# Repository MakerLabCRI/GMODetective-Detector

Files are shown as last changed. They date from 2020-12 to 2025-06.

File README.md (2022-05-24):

# GMODetective-Detector

DIY fluorescence detector for the [GMO Detective project](https://gmodetective.com/)

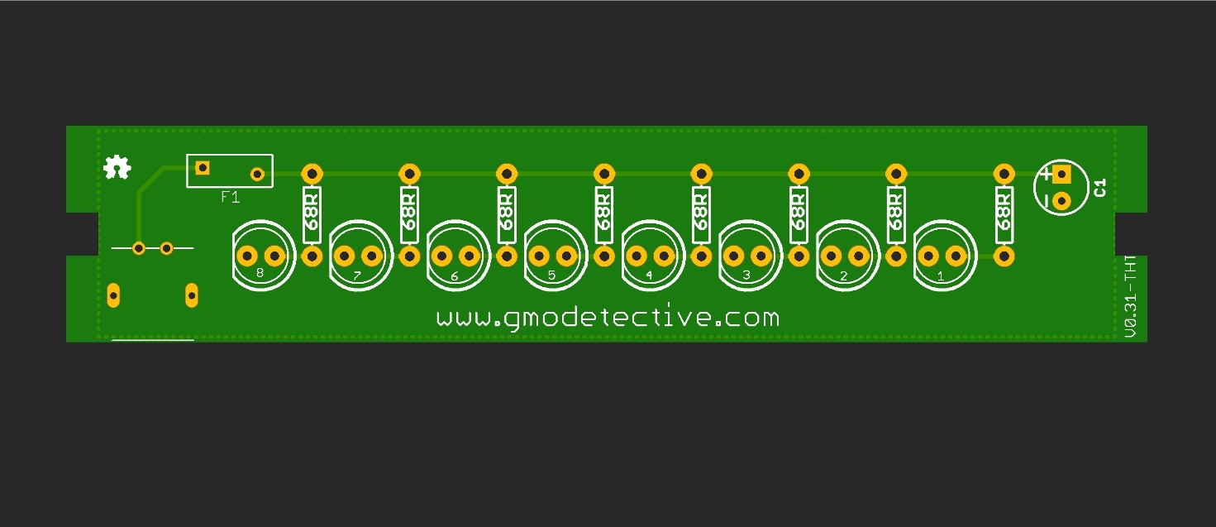
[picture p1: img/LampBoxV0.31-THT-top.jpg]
PCB view


## BOM

8x C503B-BAN-CZ0A0451 [mouser](https://www.mouser.fr/ProductDetail/Cree-Inc/C503B-BAN-CZ0A0451?qs=%2Fha2pyFaduidizlAeORLOPChSupn8qVQ9Kn4bl13zJ7nUG9%252B2UeDbT0K%252B9FgAF1f)

8x 68 ohm resistor [mouser](https://www.mouser.fr/ProductDetail/Yageo/CFR-25JT-52-68R?qs=%2Fha2pyFaduip15hodXcAQzG82qC8UTcP%2FVcFQd8KsgKmaA7VFXCJAQ%3D%3D)

1x 10uF electrolytic capacitor [mouser](https://www.mouser.fr/ProductDetail/Panasonic/ECA-1JM100B?qs=%2Fha2pyFadugf96c9oovEvKSc4mhyX5s0jUH4ND99LTDADYv5TkhqzA%3D%3D)

1x Fuse 500ma RXEF050 [mouser](https://www.mouser.fr/ProductDetail/Littelfuse/RXEF050?qs=k5V78Jg%2Feq7BserVMEB6DA%3D%3D)

1x micro USB 2P with 90° pins [Taobao](https://item.taobao.com/item.htm?spm=a230r.1.14.68.312b6bc3MnUb4G&id=597273597165&ns=1&abbucket=19#detail)
[Aliexpress](https://fr.aliexpress.com/item/4000049679173.html?spm=a2g0o.productlist.0.0.6fd1f912MCE4d2&algo_pvid=a3873bf6-c53e-42d9-8363-89ecb1d975f8&algo_expid=a3873bf6-c53e-42d9-8363-89ecb1d975f8-4&btsid=0b0a182b16071189178941562e2389&ws_ab_test=searchweb0_0,searchweb201602_,searchweb201603)
[Aliexpress (90 ° version color B or D)](https://aliexpress.com/item/4001293555150.html)
[Aliexpress (90° version color A or C)](https://fr.aliexpress.com/item/1005001515820458.html)

## 3D Model of PCB

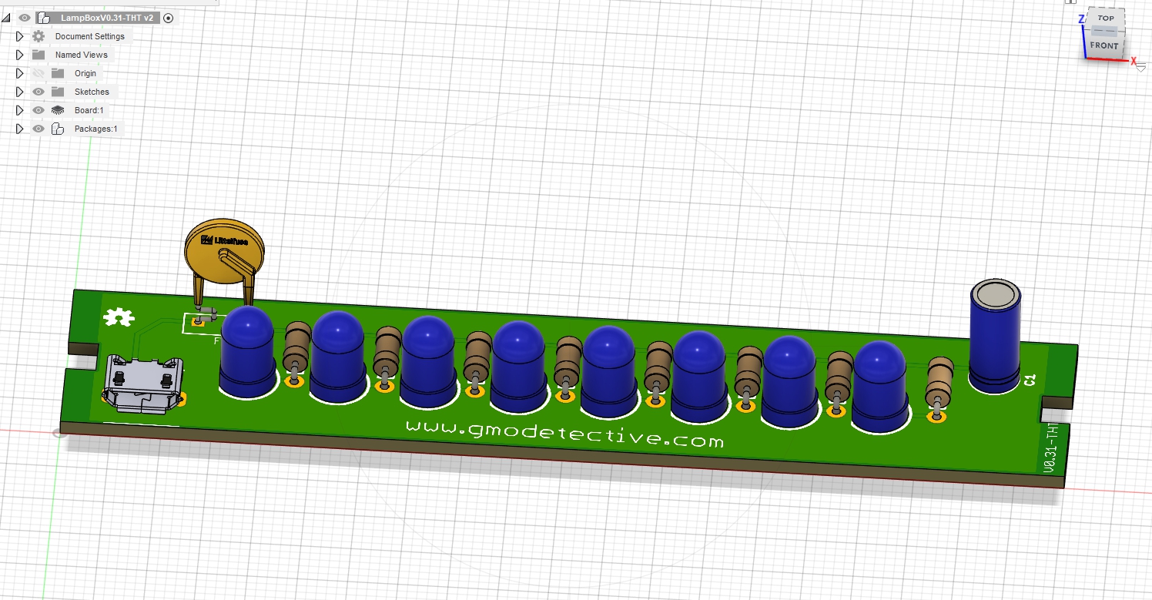
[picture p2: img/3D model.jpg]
Screengrab of 3d model


3D model

## 3d printable frame

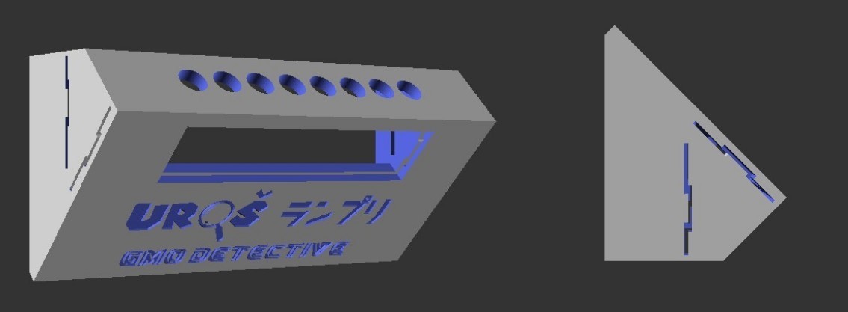
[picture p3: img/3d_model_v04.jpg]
3d model filter slit version


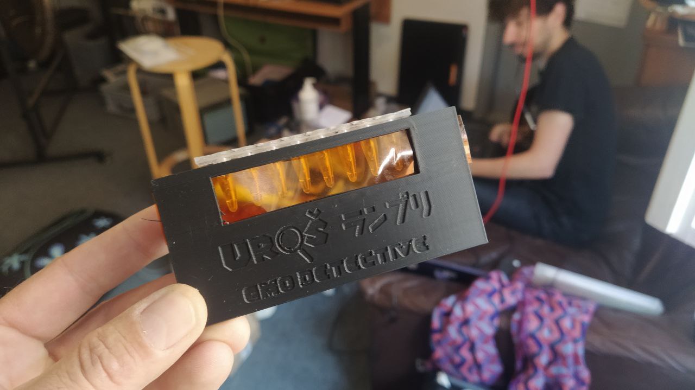
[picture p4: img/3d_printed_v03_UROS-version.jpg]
3d printed UROS version


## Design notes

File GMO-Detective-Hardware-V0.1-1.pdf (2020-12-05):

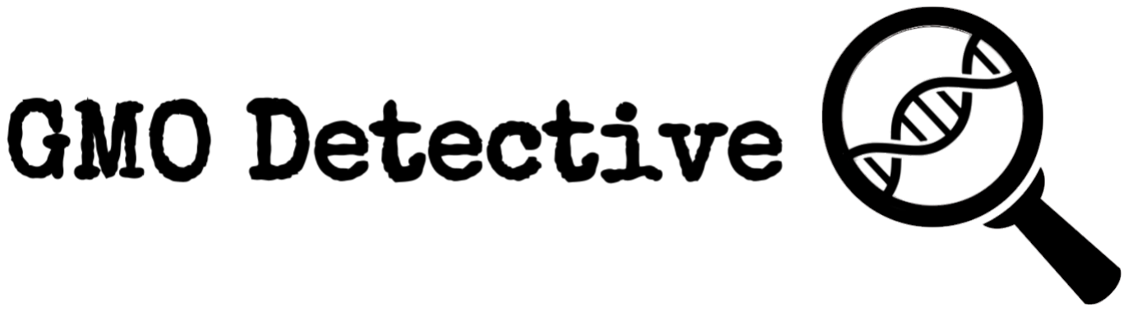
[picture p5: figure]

# Hardware Guide:

The Hardware guide will help you to gather, buy and build all the materials you need to do the experiments. This consists of reusable devices such as the open hardware fluorescence detector and also consumables which are used with each experiment.

Reusables | 1
Makabales | 1
Open Hardware Detector | 1
Holders | 2
Buyable or makeable or hackable | 3
Common materials anyone probably has: | 3
Stable heating: | 3
20 µL Pipettes | 3
Consumables | 4

# Reusables

## Makabales

Files for PCB and Laser cutter: https://gmodetective.com/wp-content/uploads/2018/10/GMOdetective_Hardware_FilesV0.1.zip (https://gmodetective.com/wp-content/uploads/2018/10/GMOdetective_Hardware_FilesV0.1.zip)

### a. Open Hardware Detector

This is a cheap DIY fluorescence detector. It is easy to build and use. A buyable version should be available soon. You will need to know how to solder as well as a soldering iron, 15x15cm 3mm plexiglass/wood, a laser cutter and the following parts:

1 PCB | https://www.pcbway.com The file is in eagle format (free for students) We can also send you some :)
8 5mm blue LEDs 470nm | https://www.mouser.com/_/?Keyword=C503B-BAN-CZ0A0451
8 68/100 ohms resistors | https://www.mouser.com/_/?Keyword=CFR-25JT-52-68R
1 Capacitor 10 F | https://www.mouser.com/_/?Keyword=ECA-1JM100B
1 Fuse 0,5 A | https://www.mouser.com/_/?Keyword=RXEF025

Orange Filters | 179 Chrome Orange ; http://www.leefilters.com/lighting/colour-details.html#179
Blue Filter | 716 Mikkel Blue : http://www.leefilters.com/lighting/colour-details.html#716

Solder the parts onto the PCB
Laser-cut the legs tube holder and front panel
Slide the PCB into the Legs
Then attach front panel and top tube holder.
Slide 1.5x11cm blue filter into leg side slits, and 2 orange filters into the smale space between the legs and front panel so you see orange through the view hole Connect to a 5v power source (USB).

### b. Holders

Laser-cut the legs and tube holder and connect

## Buyable or makeable or hackable

### Common materials anyone probably has:

You will need a mug or beaker to hold boiling water for 5 minutes during the sample prep, anything that can hold coffee or tea will do.
Aluminum foil to hold the tubes in place.
Permanent waterproof markers too, so you know what is what :)

### Stable heating:

We need something that can keep a stable 63℃

If you have a PCR machine/heat block/Scientific water bath then these will all be perfect.
Otherwise these portable sous vide vacuum cookers are perfect and affordable, and you can also experiment with new ways of cooking! https://www.aliexpress.com/item/Vacuum-Slow-Sous-Vide-Precision-Food-Cooker-1500W-Powerful-Immersion-Circulator-LCD-Digital-Timer-Display-Stainless/32869232621.html?spm=a2g0s.8937460.0.0.302d2e0eDrMWuV (https://www.aliexpress.com/item/Vacuum-Slow-Sous-Vide-Precision-Food-Cooker-1500W-Powerful-Immersion-Circulator-LCD-Digital-Timer-Display-Stainless/3286923262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)
Or

https://anovaculinary.com/
Or

### You can also make one yourself! https://www.instructables.com/howto/sous+vide/ https://www.instructables.com/id/DIY-Sous-Vide-Machines/

### 20 µL Pipettes

Buy:
https://www.aliexpress.com/item/2-20ul-Single-Channel-Adjustable-Micro-Pipette-Transfer-Pipette-Lab-Pipettor-Buy-1-Pipette-Give-50pcs/3281466128 7.html (https://www.aliexpress.com/item/2-20ul-Single-Channel-Adjustable-Micro-Pipette-Transfer-Pipette-Lab-Pipettor-Buy-1-Pipette-Give-50pcs/32814661287.html)

# Consumables

These you will need to buy. Every experiment needs: ~4 1.5mL tubes
1 PCR strip
2 Pestles
2 gloves
And ~10 tips

1,5 mL microtubes | https://www.aliexpress.com/item/1-5ml-Clear-plastic-centrifugal-t est-tube-Sample-vial-with-snap-cap-for-samples-food-colourings /32694400420.html?spm=a2g0s.9042311.0.0.3da24c4dcV9Hma (https://www.aliexpress.com/item/1-5ml-Clear-plastic-centrifugal-test-tube-Sample-vial-with-snap-cap-for-samples-food-colourings/32694400420.html)
PCR 8 tube Strips | https://www.aliexpress.com/item/200PCS-4ml-Centrifuge-Bottles-Test-Tube-With-Lid-Calibration-Round-Bottom-Seed-Container-Laboratory-Supplies-1500r/32708099906.html?spm=a2g0s.9042311.0. 0.3da24c4dcV9Hma (https://www.aliexpress.com/item/200PCS-4ml-Centrifuge-Bottles-Test-Tube-With-Lid-Calibration-Round-Bottom-Seed-Container-Laboratory-Supplies-1500r/32708099906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)
micropestles | https://www.aliexpress.com/item/50-pcs-lot-5mm-70mm-Polypropylene-Pestle-grinding-PP-rod-tip-for-1-5ml-centrifuge-tube/327620

70308.html?spm=2114.search0104.3.2.2ee51276oXfHhu&ws_ab_test= searchweb0_0,searchweb201602_3_10152_10151_10065_10344_10068_1 0342_10343_10340_10341_10696_310_10084_10083_10618_10304_10307_1 0820_10821_10302_10843_10059_100031_10103_10624_10623_10622_10621 _10620_526,searchweb201603_13,ppcSwitch_5&algo_expid=9a04db1 4-5032-4917-9edd-e21168868e7b-0&algo_pvid=9a04db14-5032-4917-9edd-e21168868e7b&priceBeautifyAB=0 (https://www.aliexpress.com/item/50-pcs-lot-5mm-70mm-Polypropylene-Pestle-grinding-PP-rod-tip-for-1-5ml-centrifuge-tube/32762070308.html?priceBeautifyAB=0)

Pipet Tips

https://www.aliexpress.com/item/New-200ul-PP-Plastic-Pipette-Tip s-For-Microbiological-Test-Pipettor-Yellow-Pipet-Tips-Disposable -Pipette-Tip/32523839777.html?spm=2114.10010108.1000014.1.6f52221c D5FWBa&gps-id=pcDetailBottomMoreOtherSeller&scm=1007.13338 .107646.000000000000000&scm_id=1007.13338.107646.00000000000000 0&scm-url=1007.13338.107646.000000000000000&pvid=982c463a-c9c 4-40ca-9c91-248ec5df68f3 (https://www.aliexpress.com/item/New-200ul-PP-Plastic-Pipette-Tips-For-Microbiological-Test-Pipettor-Yellow-Pipet-Tips-Disposable-Pipette-Tip/32523839777.html?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)

Pipet Tips in Box

https://www.aliexpress.com/item/Free-shipping-Plastic-Pipette-box-96vents-box-96pcs-200ul-yellow-pipette-tips/32595675105.html?spm=2114.10010108.1000013.1.4569761fII1muL&gps-id=pcDetailBottomMoreThisSeller&scm=1007.13339.90158.0&scm_id=1007.13339.90158.0&scm-url=1007.13339.90158.0&pvid=96b5e6cb-d67c-4218-96ed-4ef54 2c1ffcf (https://www.aliexpress.com/item/Free-shipping-Plastic-Pipette-box-96vents-box-96pcs-200ul-yellow-pipette-tips/32595675105.html?scm_id=1007.13339.90158.0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)

gloves

https://www.aliexpress.com/item/3-Sizes-High-Quality-1box-A-lotpowder-free-Nitrile-Disposable-glove-latex-Gloves-non/32845058449.html?spm=2114.10010108.1000014.16.766c662dBopRhD&gps-id=pcDetailBottomMoreOtherSeller&scm=1007.13338.106568.000000000000000&scm_id=1007.13338.106568.000000000000000&scm-url=1007.1333 8.106568.000000000000000&pvid=efecf868-310e-4497-8515-7c37fae8 2025 (https://www.aliexpress.com/item/3-Sizes-High-Quality-1box-A-lot-powder-free-Nitrile-Disposable-glove-latex-Gloves-non/32845058449.html?scm_id=1007.13338.10656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)

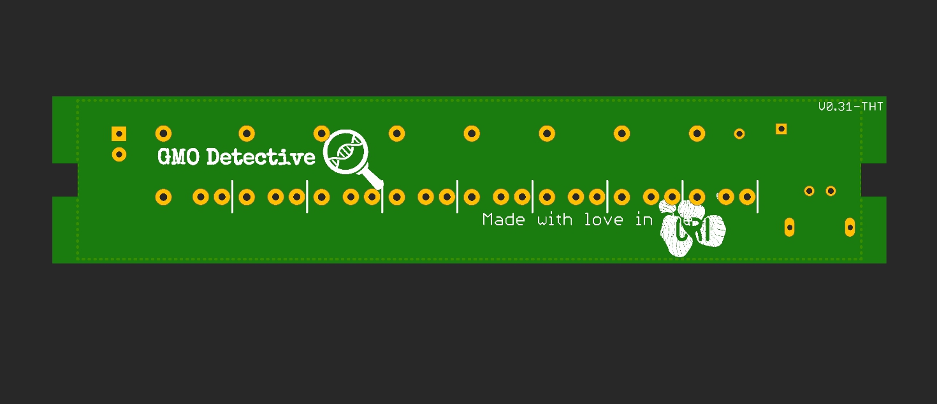
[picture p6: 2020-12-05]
img/LampBoxV0.31-THT-bottom.jpg

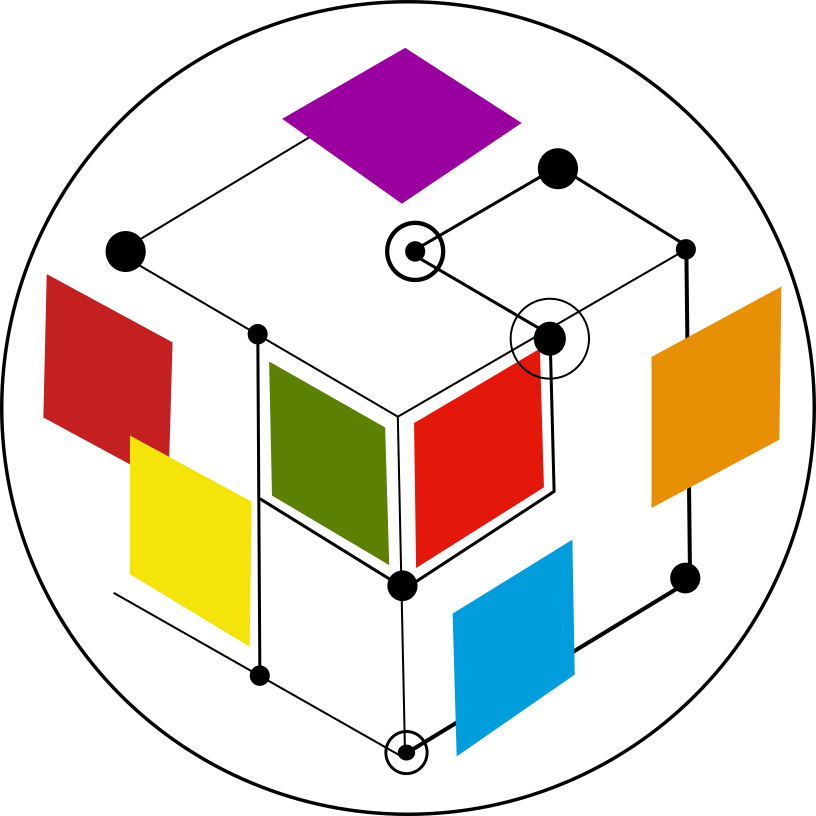
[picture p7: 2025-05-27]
3D Model/OpenScad_code/reGOSH_1.png

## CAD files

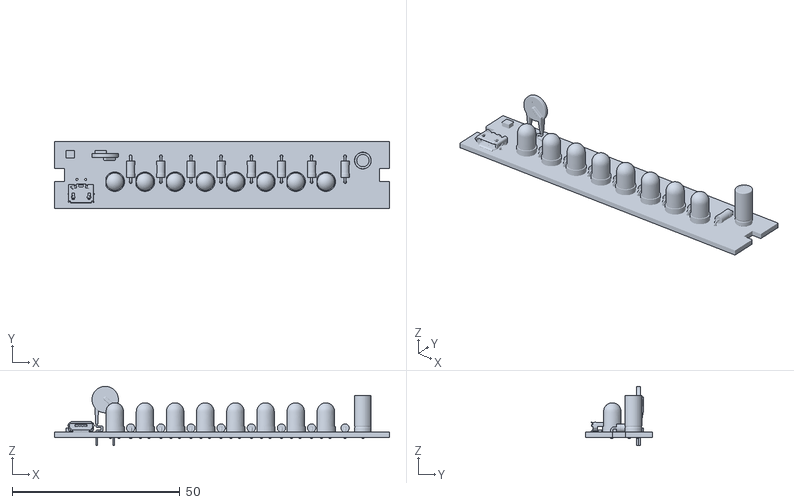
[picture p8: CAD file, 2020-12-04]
3D Model/LampBoxV0.31-THT v1.stl
100.0 x 20.0 x 17.7

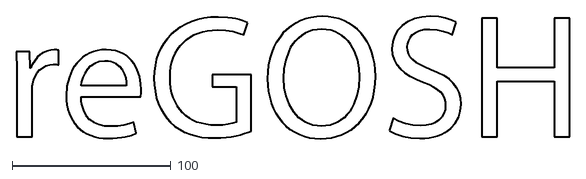
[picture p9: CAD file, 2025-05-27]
3D Model/OpenScad_code/reGOSH.dxf
349.2 x 77.1

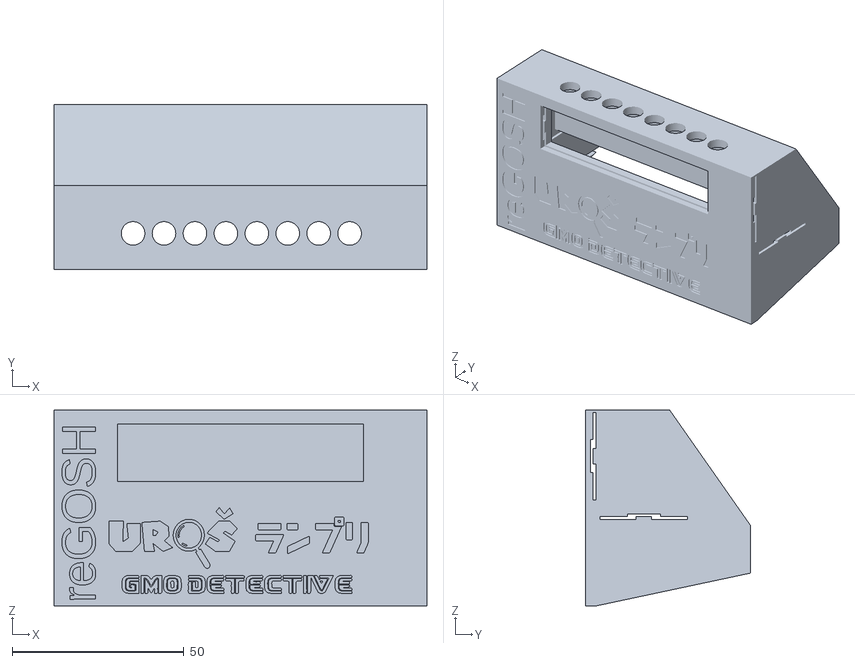
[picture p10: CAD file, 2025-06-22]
3D Model/STL/V05_GMOdetective3D_dusjagr_FF_V2.stl
108.5 x 48.0 x 57.0

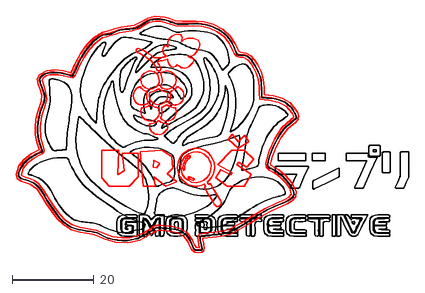
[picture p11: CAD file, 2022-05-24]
3D Model/OpenScad_code/UROS_logo.dxf
96.3 x 57.9

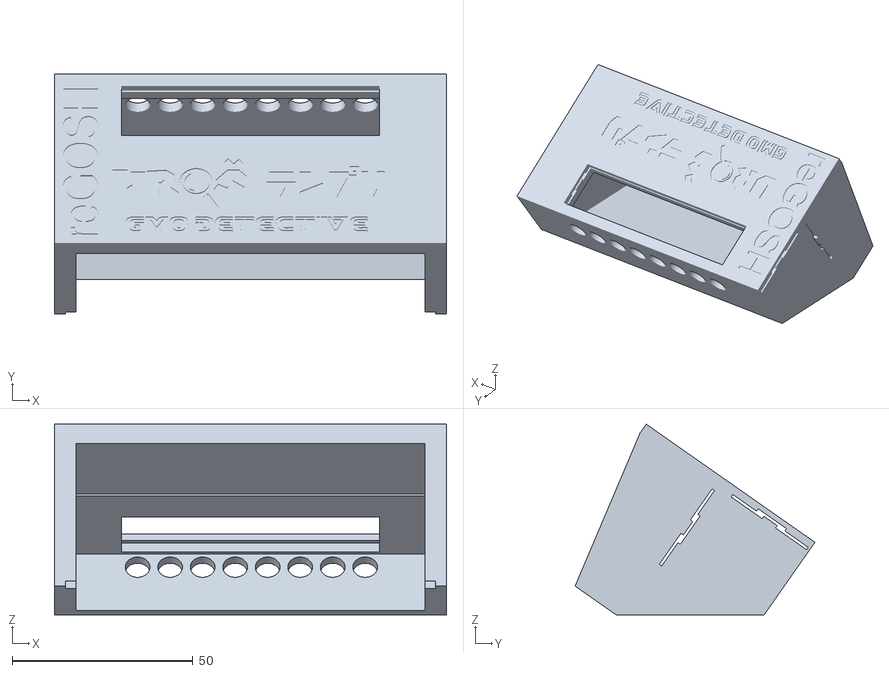
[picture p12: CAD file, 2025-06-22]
3D Model/STL/V05_GMOdetective3D_dusjagr_FF.stl
108.5 x 66.4 x 52.8

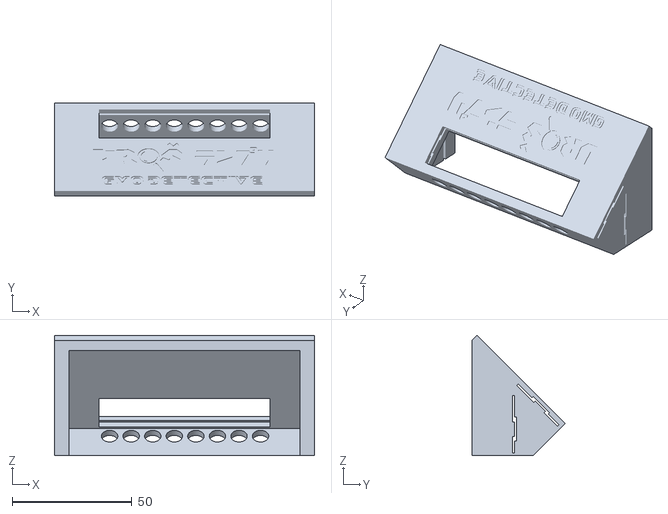
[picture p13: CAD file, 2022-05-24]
3D Model/STL/V04_GMOdetective3D_dusjagr.stl
108.5 x 38.9 x 50.2

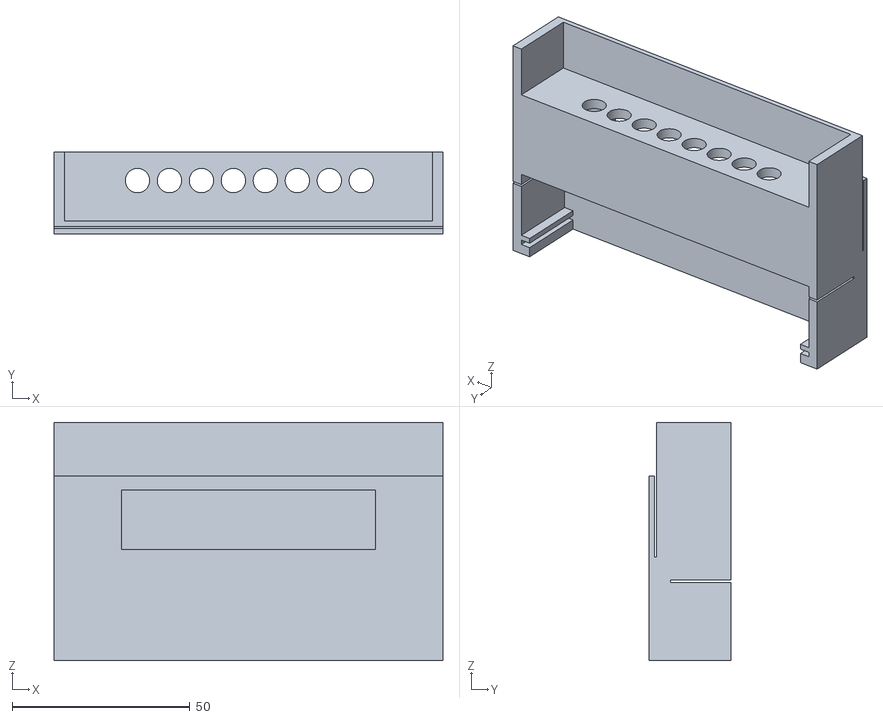
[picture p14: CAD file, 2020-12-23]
3D Model/STL/GMOdetective3D.stl
109.5 x 23.0 x 67.0

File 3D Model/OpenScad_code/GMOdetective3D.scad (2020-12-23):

/*
This file creates a 3D printed version of the acrylic GMOdetective device  developed by Guy Aidelberg 

All this code is licensed under the Creative Commons - Attribution  (CC BY 3.0)
Fernán Federici 2020

*/
         
//--------------------------parameter to play with
wd=6.85;//internal tube diameter    
xplate=127.6;
yplate=85.75;  
zplate=14.3;    
$fn=60;

dbw=9;//distance between center of tubes
sw=2;//support width
yborder_d=11.36;//distance between yborder and center first well
xborder_d=14.3;//distance between xborder and center first well
ext=10;

PCB_x=100+3.5; //this is the more important parameter, you change here and everything will scale accordingly

corr=0.2;// used for printing imperfections

PCB_y=20;
PCB_z=1.25;
notch_x=4;
notch_y=4.5;
wall=3;
front=PCB_x+wall*2;
equi_side=32;
front_height=42+ext;
depth=38+ext;
window_x=71.5;
window_h=11.8+ext/2;



//GMO3D();
module GMO3D(){
  rotate([ -45, 0, 0 ]) translate([ 0, -wall, 0]) difference(){
        cube([front, wall, front_height ]);
        //window
               translate([ (front-window_x)/2, 0, front_height-window_h-4 ]) cube([window_x, depth-wall, window_h ]);
      rotate([ 90, 0, 0 ]) translate([ 0,equi_side+wall-window_h/2, -wall]) cube([front, depth, PCB_z ]);
      }
        
difference(){
    rotate([ -45, 0, 0 ])difference(){
        cube([front, depth, front_height ]);
        //internal
        translate([ wall, wall, 0 ]) cube([front-wall*2, depth-wall, front_height-wall ]);
        //window
               #translate([ (front-window_x)/2, 0, front_height-window_h-4 ]) cube([window_x, depth-wall, window_h ]);
        //tubes
        translate([(front-window_x)/2-dbw/2,wall+dbw/2,front_height-wall]) neg_tubes();

            rotate([ 45, 0, 0 ])  translate([ 0, 0, -front_height ]) cube([front+corr, front+corr, front_height ]);
        
             translate([ 0, depth+dbw*2, 0]) rotate([ 45, 0, 0 ]) cube([front+corr, front+corr, front_height*2 ]);

        translate([ wall, wall+dbw+wall/2, 0 ]) cube([front-wall*2, depth-wall, front_height ]);

//    rotate([ 90, 0, 90 ]) linear_extrude(height = front+corr, center = false, convexity = 0, twist = 0) polygon(points=[[0,0], [38,equi_side+corr], [38,0]]);
      
    }
    //PCB slit
       translate([ 0, equi_side+dbw/2-PCB_y+ext, PCB_z+ext/2 ])         cube([PCB_x, PCB_y*2, PCB_z+corr ]); //PCB();
    //blue filter slit
    translate([ 0, equi_side-PCB_y/2, 12+ext/2 ]) cube([front, depth, PCB_z/2 ]);

        
}

    }     
    depth_sq=PCB_y+wall;
    dist_centerLEDs=12;//distance of center of LEDs and front of PCB
    LED_h=10;
    cover=15;//to cover blue light coming from top part of tubes
   win_location_h=front_height-window_h-4;
GMO3D_square_open();
    module GMO3D_square_open(){
difference(){
        union() {
            //front
            color("blue") cube([front, wall, front_height ]);
            //notches for PCB holding
                   translate([ wall, 0, 0 ])  cube([wall, depth_sq, wall*2]);
                  translate([ front-wall*2, 0, 0 ])  cube([wall, depth_sq, wall*2 ]); 
            }
 
        //window
               translate([ (front-window_x)/2, 0, front_height-window_h-4 ]) cube([window_x, depth-wall, window_h ]);
    //orange filter
translate([ 0,wall/2, front_height-window_h*1.5]) cube([front, PCB_z/2, window_h*2 ]);
            
    //PCB slit 
       translate([ wall, wall, wall ])  cube([PCB_x, PCB_y*3, PCB_z+corr ]); 
  //PCB alignment used to check holes and LEDs are aligned
        #translate([ wall, wall, wall ]) PCB();
      }
difference(){
       color("red") cube([front, depth_sq, front_height ]);

    
        //internal
        translate([ wall, wall, 0 ]) cube([front-wall*2, depth-wall, front_height-wall ]);
        //window
           translate([ (front-window_x)/2, 0, win_location_h ]) cube([window_x, depth-wall, window_h ]);
        //tubes 
    //(considering that there is 12mm from center of LEDs to front of PCB, so in order to align tubes and LEDs, this distance should be considered carefully
        translate([(front-window_x)/2-dbw/2,wall+dist_centerLEDs,front_height-wall]) neg_tubes();
    //blue filter slit
    translate([ 0, wall*2, 12+ext ]) cube([front, depth, PCB_z/2 ]);   
   //orange filter
#translate([ 0,wall/2, win_location_h-2]) cube([front*1.1, PCB_z/2, window_h*2 ]);
    }
      //cover
    translate([ 0, wall/2+PCB_z/2, front_height ]) 
    difference(){    
      color("red")  cube([front, depth_sq-wall/2-PCB_z/2, cover ]);
         translate([ wall, wall/2, 0 ])  color("yellow")  cube([front-wall*2, depth_sq-wall, cover ]);
        }
                  translate([ 0, depth_sq-wall, front_height/2])  cube([front, wall, front_height/2 ]);
    }     
    
    
//  GMO3D_square_clopen();  
  module GMO3D_square_clopen(){
 
    }     
    
    module clopen_rear(){
           //bottom
    translate([ 0, depth_sq, front_height/2])  cube([front, wall, front_height/2 ]);
}
    
//GMO3D_square();
module GMO3D_square(){
 difference(){
        union() {cube([front, wall, front_height ]);
                   translate([ wall, 0, 0 ])  cube([wall, depth_sq, wall*2]);
                  translate([ front-wall*2, 0, 0 ])  cube([wall, depth_sq, wall*2 ]); 
            }
 
        //window
               translate([ (front-window_x)/2, 0, front_height-window_h-4 ]) cube([window_x, depth-wall, window_h ]);
    //orange filter
translate([ 0,wall/2, front_height-window_h*1.5]) cube([front, PCB_z/2, window_h*2 ]);
            
    //PCB slit 
       #translate([ wall, wall, wall ])  cube([PCB_x, PCB_y*3, PCB_z+corr ]); 
  //PCB alignment
        #translate([ wall, wall, front_height-wall*4 ]) PCB();
      }
difference(){
        cube([front, depth_sq, front_height ]);
        //internal
        translate([ wall, wall, 0 ]) cube([front-wall*2, depth-wall, front_height-wall ]);
        //window
           translate([ (front-window_x)/2, 0, front_height-window_h-4 ]) cube([window_x, depth-wall, window_h ]);
        //tubes 
    //(considering that there is 12mm from center of LEDs to front of PCB, so in order to align tubes and LEDs, this distance should be considered carefully
        translate([(front-window_x)/2-dbw/2,wall+dist_centerLEDs,front_height-wall]) neg_tubes();
    //blue filter slit
    #translate([ 0, wall, 12+ext ]) cube([front, depth, PCB_z/2 ]);   
   //orange filter
translate([ 0,wall/2, front_height-window_h*1.5]) cube([front, PCB_z/2, window_h*2 ]);
    }
     

    }     
    
//PCB();    
module PCB(){
    difference(){
        cube([PCB_x, PCB_y, PCB_z+corr ]);
   
       #translate([ 0, PCB_y/2-notch_y/2, 0 ]) cube([notch_x, notch_y, PCB_z+corr ]);   
    }
       translate([(front-window_x)/2-dbw/2-wall,dist_centerLEDs,0])   LEDs();}     
    

module LEDs(){
   for(x = [1:8]){
						// tube holes
						translate([x*dbw,0,LED_h/2])
						color("orange") cylinder (h=LED_h, r = 5/2, center=true);	
       }}




 module neg_tubes(){
				for(x = [1:8]){
						// tube holes
						translate([x*dbw,0,0])
						color("orange") cylinder (h=zplate+corr, r = wd/2, center=true);	
                          }}   
    

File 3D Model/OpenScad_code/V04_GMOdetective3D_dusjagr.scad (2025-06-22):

/*
This file creates a 3D printed version of the acrylic GMOdetective device  developed by Guy Aidelberg 

All this code is licensed under the Creative Commons - Attribution  (CC BY 3.0)
Fernán Federici 2020

Modified for UROŠ - Ubiquitous Rural Open Science Hardware
- modded slits for the filters to hold better
dusjagr Okt 2021

*/
         
//--------------------------parameter to play with
wd=6.85;//internal tube diameter    
xplate=127.6;
yplate=85.75;  
zplate=14.3;    
$fn=60;

dbw=9;//distance between center of tubes
sw=2;//support width
yborder_d=11.36;//distance between yborder and center first well
xborder_d=14.3;//distance between xborder and center first well
ext=10;

filterSlit_thickness=0.8; // for flexible filters to squeeze them in

PCB_x=100+2.5; //this is the more important parameter, you change here and everything will scale accordingly

corr=0.2;// used for printing imperfections

PCB_y=20;
PCB_z=1.25;
notch_x=4;
notch_y=4.5;
wall=3;
front=PCB_x+wall*2;
equi_side=32;
front_height=47+ext;
depth=38+ext;
window_x=71.5;
window_h=11.8+ext/2;
    
depth_sq=PCB_y+wall;
dist_centerLEDs=12;//distance of center of LEDs and front of PCB
LED_h=10;
cover=15;//to cover blue light coming from top part of tubes
win_location_h=front_height-window_h-4;
    
/////////////////////////-----------rendering

//first design. It works.
//GMO3D_square_open();


//collaborative design. Render it like this for better printing without support materials
//color("DeepPink",0.75) rotate([ -90-45+10, 0, 0 ]) GMO3D();

/////////////////////////-----------modules


module UROS_logo(){
    linear_extrude(height = 1, center = false, convexity = 10) import(file = "UROS_logo.dxf", layer = "uros_logo");   
    linear_extrude(height = 1, center = false, convexity = 10) import(file = "UROS_logo.dxf", layer = "GMO_detective");  
    
}

//reGOSH();
module reGOSH(){
    linear_extrude(2)
text( "reGOSH");
     
    
}


//translate([ wall, wall*3-PCB_y/2, PCB_z+ext -2])   PCB();  
//GMO3D();
module GMO3D(){
  translate([ 0, -wall, 0]) difference(){
        // front plate
     color("DeepPink")   cube([front, wall, front_height ]);
      
        // emboss logos
        rotate([ 90, 0, 0 ]) translate([ 0,0, -0.5]) UROS_logo();
       rotate([ 90, 0, 0 ]) translate([ 12,1, -0.5]) rotate([0,0,90])reGOSH();
        //window
        translate([ (front-window_x)/2, -1, front_height-window_h-4 ]) cube([window_x, depth-wall+1, window_h ]);
//      //orange filter slit
//     rotate([ 90, 0, 0 ])  translate([ 0,equi_side+wall-window_h/2, -wall]) cube([front, depth/2, filterSlit_thickness ]);
//      rotate([ 90, 0, 0 ]) translate([-1,equi_side+wall-window_h/2+8, -wall+filterSlit_thickness]) cube([front+2, depth/5, filterSlit_thickness ]);      
            
      //orange filter slit 
        translate([ 0,0,  front_height-window_h-4-equi_side]) rotate([ 90, 0, 0 ]) union(){translate([ 0,equi_side+wall-window_h/2+depth/2-depth/4+wall, -wall]) cube([front, depth/4-wall/2, filterSlit_thickness ]);
      translate([ 0,equi_side+wall-window_h/2, -wall]) cube([front, depth/4-wall/2, filterSlit_thickness ]);
       translate([-1,equi_side+wall-window_h/2+8, -wall+filterSlit_thickness]) cube([front+2, depth/5, filterSlit_thickness ]);}    
     }
     
////orange filter slit holder
// translate([ 0, -wall, 0]) difference(){     
//    rotate([ 90, 0, 0 ]) translate([0,equi_side+wall-window_h/2+10, -wall]) cube([front, depth/8, filterSlit_thickness]);    
//    translate([ (front-window_x)/2, 0, front_height-window_h-4 ]) cube([window_x, depth-wall, window_h ]);
//}
 
difference(){
    difference(){
       color("DeepPink",0.75) cube([front, depth-wall, front_height ]);
              
         //blue filter slit
      translate([ 0,-equi_side+wall-window_h/2+depth/2-depth/4, front_height-window_h-12 ]) union(){ translate([ 0,equi_side+wall-window_h/2+depth/2-depth/4+wall, -wall]) cube([front+3, depth/4-wall/2, filterSlit_thickness ]);
      translate([ 0,equi_side+wall-window_h/2, -wall]) cube([front+3, depth/4-wall/2, filterSlit_thickness ]);
       translate([-1,equi_side+wall-window_h/2+8, -wall+filterSlit_thickness]) cube([front+3, depth/5, filterSlit_thickness ]);}
       
        //internal
       difference(){ translate([ wall*2, wall, 0 ]) cube([PCB_x-wall*2, depth-wall, front_height-wall ]);
           translate([ -0.5, depth+dbw*2-wall*2.5, 2]) rotate([ 35, 0, 0 ]) cube([1+front+corr, front+corr, front_height*2 ]);
    }
        //window
        translate([ (front-window_x)/2, -1, front_height-window_h-4 ]) cube([window_x, depth/3, window_h ]);
        //tubes
        translate([(front-window_x)/2-dbw/2,wall+dbw/2,front_height-wall]) neg_tubes();
        // cut bottom
        rotate([ 12, 0, 0 ])  translate([ -0.5, 0, -front_height ]) cube([1+front+corr, front+corr, front_height ]);
         // cut behind
        translate([ -0.5, depth+dbw*2-wall*2, 2]) rotate([ 35, 0, 0 ]) cube([1+front+corr, front+corr, front_height*2 ]);
      
    }
//    //PCB slit
//    translate([ wall, equi_side+dbw/2-PCB_y+ext, PCB_z+ext/2 ]) cube([PCB_x, PCB_y+5, PCB_z+corr ]); 
    
     //PCB slit oblique
      translate([ wall, wall, PCB_z+ext-2 ]) cube([PCB_x, PCB_y+50, PCB_z+corr ]); 
//    //blue filter slit
//   %  union(){ translate([ 0, 1+equi_side-PCB_y/2, 12+ext/2 ]) cube([front, depth/2, filterSlit_thickness ]);    
//    translate([ -1, equi_side, filterSlit_thickness+12+ext/2 ])   cube([front+2, 10, filterSlit_thickness ]);   
//   } 
    }

////PCB click-in   
//difference(){   
//translate([ 0, equi_side+dbw/2-PCB_y+ext+8.5, PCB_z+ext/2 ]) cube([front, 3.8, 0.32]);
//   translate([ wall*2, wall, 0 ]) cube([PCB_x-wall*2, depth-wall, front_height-wall ]); 
//   } 

   
  
}
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

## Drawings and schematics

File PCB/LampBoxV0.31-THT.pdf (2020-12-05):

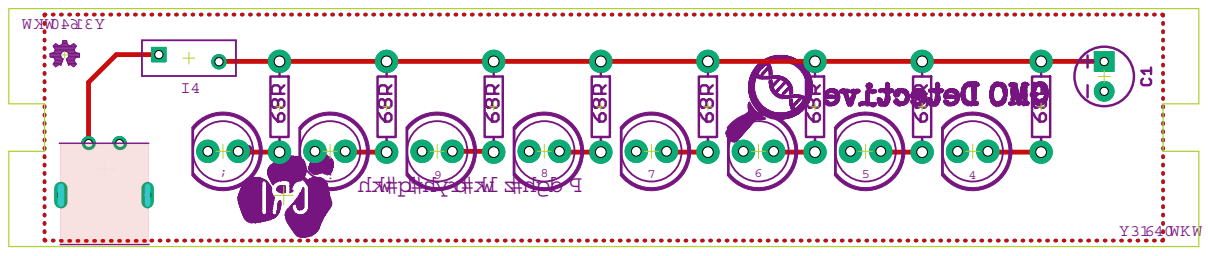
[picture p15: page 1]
V0.31-THT

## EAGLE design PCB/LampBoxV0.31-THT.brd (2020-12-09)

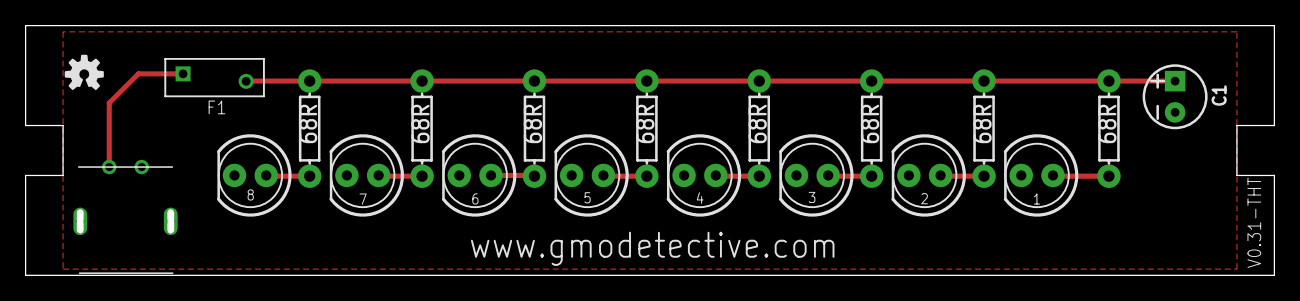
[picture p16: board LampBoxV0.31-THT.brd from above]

Board: 2 copper layers, 100.0 x 20.0 mm, 22 parts (1 on the bottom side), 11 nets.

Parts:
1, 2, 3, 4, 5, 6, 7, 8: LED_5MM
C1: 10UF-POLARGMODETECTOR; CPOL-RADIAL-2.5MM-5MM
F1: LITTELFUSE_RXEF050LITTELFUSE_RXEF050_0_0; LITTELFUSE_RXEF050_0
LOGO2: OSHW-LOGOS; OSHW-LOGO-S
R1, R2, R3, R4, R5, R6, R7, R8: 68R; AXIAL-0.3
U$2: LOGO_GMO_DETECTIVENEW; LOGO_GMO_DETECTIVE
U$3: LOGO-CRI-NEW-110MM-BOTTOM-SILK; LOGO_CRI-NEW-BMP10MM-BOTTOM
U$4: USB-2P; MICRO-USB2P-TB1

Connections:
+5V: C1.1, F1.2, R1.P$1, R2.P$1, R3.P$1, R4.P$1, R5.P$1, R6.P$1, R7.P$1, R8.P$1
GND: 1.K, 2.K, 3.K, 4.K, 5.K, 6.K, 7.K, 8.K, C1.2, U$4.GND
unnamed: 1.A, R1.P$2
unnamed: 2.A, R2.P$2
unnamed: 3.A, R3.P$2
unnamed: 4.A, R4.P$2
unnamed: 5.A, R5.P$2
unnamed: 6.A, R6.P$2
unnamed: 7.A, R7.P$2
unnamed: 8.A, R8.P$2
VIN: F1.1, U$4.5V

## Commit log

2020-12-04 added eagle files
    [LampBoxV0.31-THT.brd, LampBoxV0.31-THT.sch]
2020-12-04 updated pcb files and readme
    [LampBoxV0.31-THT v1.stl, LampBoxV0.31-THT.brd]
2020-12-05 cosmetic improvements
    [LampBoxV0.31-THT.brd]
2020-12-09 updated repi structure
    [LampBoxV0.31-THT.brd]
2020-12-23 openscad code
    [GMOdetective3D.scad, GMOdetective3D.stl]
2021-10-21 adding dusjagr's modded version for 3d printing
    [GMOdetective3D_V02_dusjagr.scad, GMOdetective3D_V02_dusjagr.stl, UROS_logo.dxf, V03_GMOdetective3D_dusjagr.scad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]
2021-10-21 cleaning some files
    [GMOdetective3D_V02_dusjagr.scad, GMOdetective3D_V02_dusjagr.stl, V03_GMOdetective3D_dusjagr.stl]
2021-11-15 thinner sidewalls
    [V03_GMOdetective3D_dusjagr.stl, V04_GMOdetective3D_dusjagr.scad, V04_GMOdetective3D_dusjagr.stl]
2021-11-15 v04 of 3dprintable reader, fixed
    [V04_GMOdetective3D_dusjagr.scad, V04_GMOdetective3D_dusjagr.stl]
2025-05-27 STL and new design
    [V04_GMOdetective3D_dusjagr.scad, V05_GMOdetective3D_dusjagr_FF.stl, reGOSH.dxf]
2025-06-22 STL and new design 2
    [V04_GMOdetective3D_dusjagr.scad, V05_GMOdetective3D_dusjagr_FF.stl, V05_GMOdetective3D_dusjagr_FF_V2.stl]
